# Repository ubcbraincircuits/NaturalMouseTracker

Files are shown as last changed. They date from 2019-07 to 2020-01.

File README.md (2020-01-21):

# MouseTrackingSystem
A system for using RFID tags and computer vision to track multiple mouse movement within a small environment.
For more detailed information, please check the [wiki!](https://github.com/ubcbraincircuits/NaturalMouseTracker/wiki)
For a brief overview, read on!

## RFID System
Uses 4 ID-20LA RFID tag readers, which then interface with the Raspberry Pi with serial communication.
The tag readers are set up in the four corners of the cage, to minimize electromagnetic interference. This system is constantly running in parallel with the Overhead Camera, recording each tag read with respect to frames of the video.

## Overhead Camera
Records videoa at 15.0 fps, converts to grayscale, and saves for use in the object detection system.

## YOLO
An object detection system trained in-house using https://pjreddie.com/darknet/yolo/. Stands for "You Only Look Once" - this system is very fast and accurate, and only fails when mice climb completely atop one another, or are obscured from the camera's vision. The information from the object detection system feeds into the Mouse Trackers.

## Mouse Trackers
When the detection system sees as many objects as there are mice, then the system simply tracks based on Euclidean distance, choosing the closest pairs of detections until all mice and detections are covered. Since the framerate is faster than the mouse movement, this is a reliable method for tracking all mice. When mice are lost, a mouse is removed from the main list and a "dummy mouse" is added in place - so, if two mice are lost, then they are replaced with dummy mice henceforth. Once the mice return, the RFID system is checked continuously. Once we have found a frame in which a mouse has been read by the RFID sensors, the dummy mice are classified and the system is retroactively corrected. In this way, even though we may not be certain of which mouse is which on every frame moving forwards in time, once the system has finished running, all mice movement will have been completely tracked.

### RFID Validation
RFID validation is used to correct and update the current state of the system. If an identity swap occurs that is not handled by the preventative destruction method, then there must be countermeasures. Thus, if a mouse identified by the system as tracked walks over an RFID sensor and is shown to be a different tag, then its data must be removed up to the last validation point, i.e. the last point it was confirmed by an RFID sensor. 

By combining these methods, we can confirm no identity swaps and an 80%+ coverage rating for this system.

### Sources
- https://github.com/Ebonclaw/Mouse-Wearable-Tech---RFID-and-Localization-Grid-Computer-Vision-Enhancement - original inspiration
- https://github.com/AlexeyAB/darknet - object detection 
- https://github.com/jamieboyd/RFIDTagReader - tag reader

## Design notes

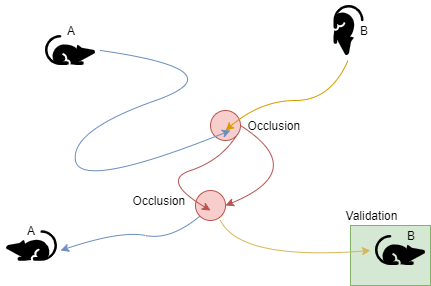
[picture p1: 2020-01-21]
SwapHandling-Page-2.png

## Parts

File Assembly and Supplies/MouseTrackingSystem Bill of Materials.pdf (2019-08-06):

Item | Quantity | Supplier | Individual Cost | Total Cost Part Number
N10 Mouse Cage | 3 Ancare | N/A | N/A | N/A
ID-20LA | 12 SparkFun | $ | 34.95 $ | 419.40 | 11828
RFID USB Reader | 12 SparkFun | $ | 25.18 $ | 302.16 | 9963
Zinc-Plated Alloy Steel
Socket Head Screw,
1/4"-20 x 1" | 3 McMaster-Carr $ | 6.37 $ | 6.37 90128A247
M3 (16mm) 18-
8 Stainless Steel Socket
Head Screw | 100 (pack) McMaster-Carr N/A | $ | 5.87 91292A115
M3 Medium-Strength Steel
Hex Nuts—Class 8 | 100 (pack) McMaster-Carr N/A | $ | 0.88 90592A085
Steel Pan Head Phillips
Screw, M2.5 x
0.45 mm Thread, 12
mm Long | 100 (pack) McMaster-Carr N/A | $ | 4.66 92005A075
M3 (12mm) 18-
8 Stainless Steel Socket
Head Screw | 100 (pack) McMaster-Carr N/A | $ | 4.97 91292A115
M2 (12mm) 18-
8 Stainless Steel Socket
Head Screw | 100 (pack) McMaster-Carr N/A | $ | 4.02 91292A834
M2 Medium-Strength Steel
Hex Nuts—Class 8 | 100 (pack) McMaster-Carr N/A | $ | 1.47 90592A075
M2 Medium-Strength Steel
Hex Nuts—Class 8 | 100 (pack) McMaster-Carr N/A | $ | 1.94 90592A080
RPi Camera (H), Fisheye
Lens, Supports Night
Vision | 3 Waveshare | $ | 31.59 $ | 94.77 | 10703
Raspberry Pi 4/3 B+ | 3 CanaKit | $ | 46.95 $ | 140.85 N/A
| | TOTAL | $ | 987.36
| | Av. Cost | $ | 329.12

Link
http://www.ancare.com/products/cages-and-caging-equipment/rodent-cage/mouse-cagehttps://www.sparkfun.com/products/11828
https://www.sparkfun.com/products/9963

https://www.mcmaster.com/90128A247

https://www.mcmaster.com/91292a115

https://www.mcmaster.com/90592A085

https://www.mcmaster.com/92005A075

https://www.mcmaster.com/91292a115

https://www.mcmaster.com/91292a834

https://www.mcmaster.com/90592A075

https://www.mcmaster.com/90592A080

https://www.waveshare.com/product/mini-pc/raspberry-pi/cameras/rpi-camera-h.htmhttps://www.canakit.com/raspberry-pi-4.html

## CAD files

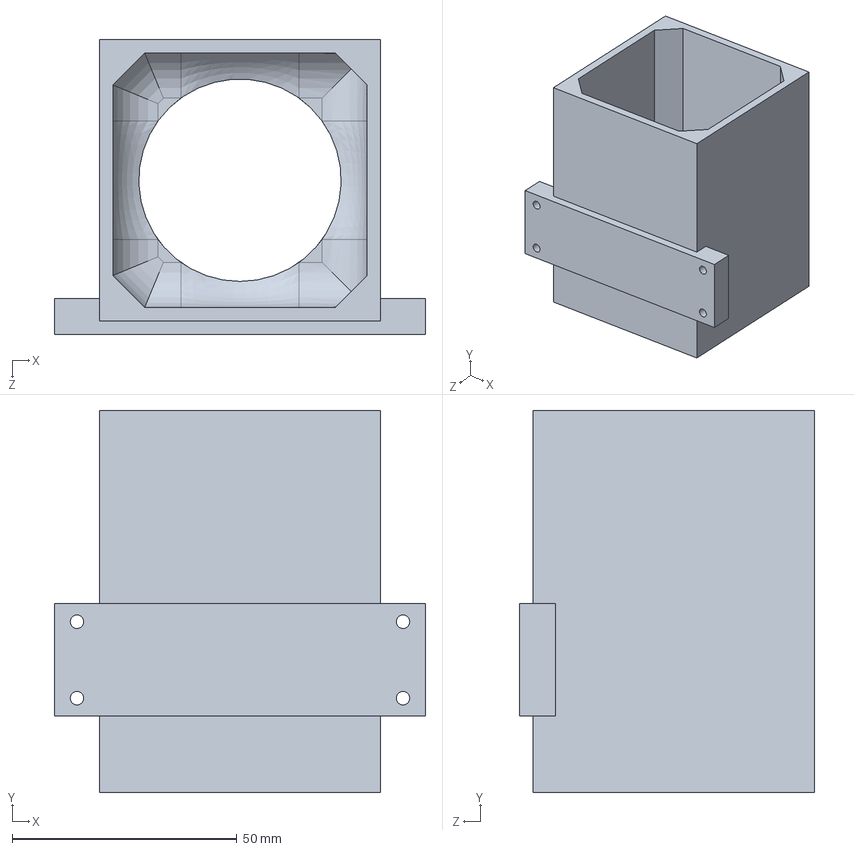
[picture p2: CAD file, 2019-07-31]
CAD Files/WaterBottleHolster.SLDPRT
82.5 x 85.0 x 65.5 mm

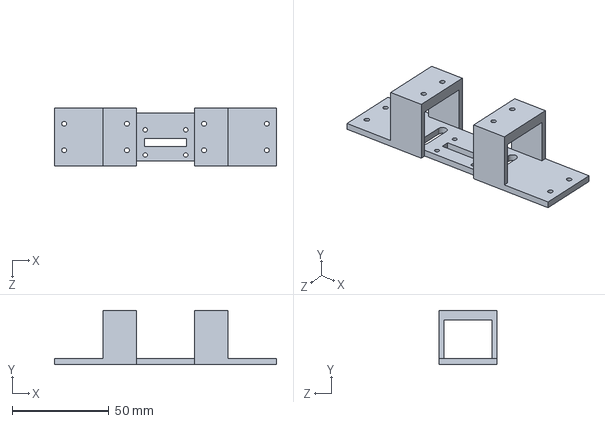
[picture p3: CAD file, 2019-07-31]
CAD Files/Camera LED Mount.SLDPRT
115.0 x 28.0 x 30.0 mm

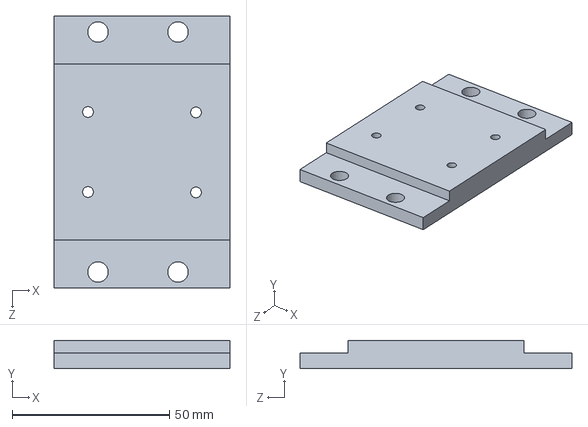
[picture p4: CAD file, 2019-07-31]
CAD Files/Reader Base.SLDPRT
55.9 x 9.00 x 86.4 mm

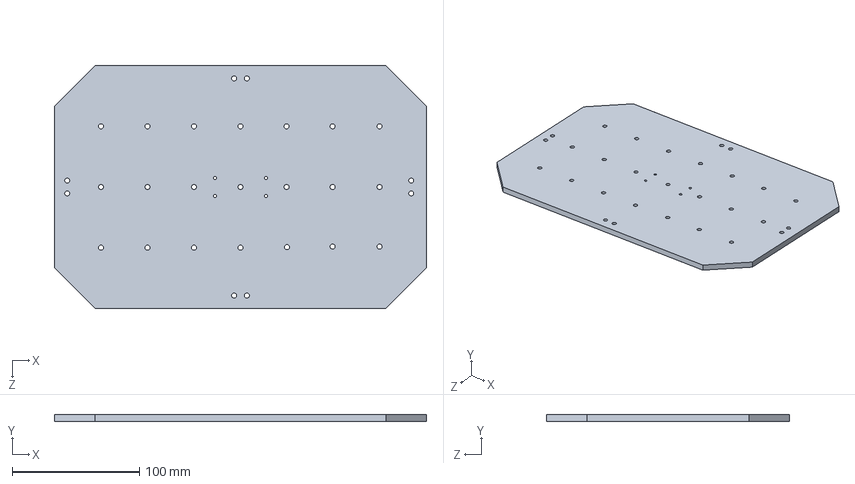
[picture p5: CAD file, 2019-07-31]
CAD Files/Lid.SLDPRT
292.1 x 5.30 x 190.5 mm

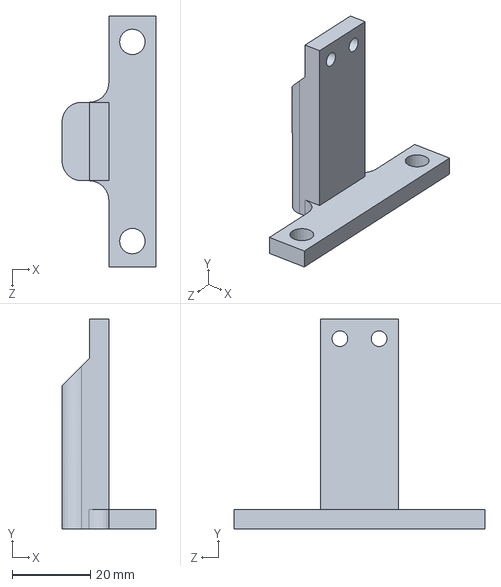
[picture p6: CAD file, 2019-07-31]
CAD Files/Base Attachment.SLDPRT
23.9 x 53.5 x 64.0 mm

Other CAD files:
CAD Files/Base Attachment.STL
CAD Files/Camera LED Mount.STL
CAD Files/Lid.DXF
CAD Files/Reader Base.STL
CAD Files/WaterBottleHolster.STL

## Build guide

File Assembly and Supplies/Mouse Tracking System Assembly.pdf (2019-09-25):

# Mouse Tracking System: Assembly Instructions

## You Will Need:

- A computer with (at minimum) a GPU with 4GB of GPU-RAM
- Access to a 3D printer and a supply of PLA
- Laboratory mice with implanted RFID tags
- Access to a laser/waterjet cutter and ¼” acrylic
- 1 ThorLabs metal platform (fits 3 cages)
- Everything listed in the Bill of Materials

### Step 0: Preparation

a) I recommend cutting the lid piece ahead of time. Make an order with your machine shop (or cut your own, if you can). The air holes do not have to be exact – the screw holes should be relatively precise, which is why I do not recommend doing this by hand. If doing this by hand, measure very carefully and use a drill press to form the holes.
b) Print the 3D-printed pieces: This will take a while, likely overnight, and may take a few passes to fit all the pieces. Ensure you print the water bottle holster in white if you can.
c) Drill 2 3mm holes on each short side of the cage, 25 mm above the floor. Use the base attachment piece as a reference.
d) Drill 4 2.5mm holes on one side of the cage, to match the water bottle holster.

### Step 1: Mechanical Assembly

a) Start with the reader bases. Place the 12mm length M3 bolts through the holes in each breakout board, and screw 4 nuts on the backside to act as spacers. Mount each board on its respective reader, and screw another 4 nuts to fasten them firmly. Repeat for each breakout board.
b) Place the two base attachment pieces with 10 holes (exclusive) between them, flat sides facing inward. Screw them into the platform with the ¼”-20 bolts. The cage should fit nicely between them – if not, count again.
c) Place each reader base with the outward hole side in line with the base attachment piece holes: there should be a line of 6 holes, with the base attachment piece in the middle. These pieces will form the four corners of the cage. Carefully, taking care that the bases stay flush with the platform, screw them in with more ¼”-20 bolts. Alternating the bolt you are screwing in will make this an easier process.
d) Place each RFID reader on its respective breakout board.
e) Either paint the exterior of the cage with nonhazardous white paint, or tape printer paper over the sides, much in the same way as wrapping a package. This ensures a better background for the mice to be seen on. Place the cage on the readers and line up the holes with the base attachment – screw in the 16mm M3 bolts and thread the nuts on the exterior of the cage. The readers should be gently pressing against the floor of the cage.
f) Screw in the camera and LEDs to the mount with the M2/M2.5 bolts, then screw the mount to the lid in the center of the cage.

### Step 2: Software Setup

a) Clone https://github.com/Judge24601/MouseTrackingSystem.git to both your Raspberry Pi and the computer you plan to use for processing the videos. (git clone …)
b) Follow the instructions in https://github.com/AlexeyAB/darknet ‘s README for installing darknet. If using CUDA 10.1, edit the .vcxproj files in build/darknet with a text editor to replace 10.0 with 10.1 – this is necessary or the system will not compile.
c) Unzip darknet.zip in the MouseTrackingSystem folder on your computer. Move the files
darknet_video.py, MouseTracker.py, visualize.py into the darknet folder.
d) If using black mice, you can use the pretrained weights in the repository. Move yolo-obj_best.weights into the folder as well. Otherwise, you will need to train your own network. Follow the instructions in https://github.com/AlexeyAB/darknet to do so. Ensure you prepare 2000+ good quality images – I recommend including non-mouse objects of a similar size and shape to your mice in the dataset. Otherwise, the network can rely too heavily on contrast.

### Step 3: Running the System

a) Before plugging in all your USB cables, ensure that you have set up SSH on your Pi – running the system headless will achieve a better framerate.
b) Plug in your external hard drive, and run the following commands:
a. sudo apt-get update
b. sudo lsblk -o UUID,NAME,FSTYPE,SIZE,MOUNTPOINT,LABEL,MODEL
(note the location, UUID, and FSTYPE of your HDD)
c. (if FSTYPE is EXFAT) sudo apt-get install exfat-fuse
d. (if FSTYPE is NTFS) sudo apt-get install ntfs-3g
e. sudo mkdir /mnt/frameData
f. sudo nano /etc/fstab
g. Add the following line: UUID=<UUID> /mnt/frameData <FSTYPE> defaults,auto,umask=000,users,rw,nofail 0 0
h. Exit nano and sudo reboot
i. This will mount your external hard drive on the Pi automatically upon connection.
j. For any problems, check https://www.raspberrypi.org/documentation/configuration/external-storage.md.
c) Do a test run of the program with a sample RFID tag. Hover the tag over the 4 readers in sequence, and note this sequence. Open the results file, and adjust the readerMap in RFIDReader.py so that it matches the actual sequence. This must be done each time the USBs are unplugged, but not as long as they remain plugged in.
d) Put the mice in the cage, along with food and water. Place the lid with the camera mount on top.
e) To preview the video and check lighting, run preview.sh through ssh. This will open up a stream that you can view on any computer with VLC Media Player (Media -> Open Network
Stream -> rtsp://:8554 )
f) Through ssh, run python RFIDReader.py – let the system run for as long as you want to collect data for. When done, use Ctrl-C to stop the program.

g) Save the photos onto a hard disk drive, and transfer them to your computer. Copy the files you wish to use into “MouseTrackingSystem/darknet/frameData” and copy the RTS_test.txt file into “MouseTrackingSystem/darknet”.
h) Run python darknet_video.py, and enter the tags for your mice.
i) Return later to find a JSON file with all the processed data!

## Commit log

2019-05-16 Arduino complete and 2.25x faster Python
2019-07-05 More framerate improvments
2019-07-09 Removed freezing and duplicate frames
2019-07-30 CAD Files
    [Base Attachment.SLDPRT, Base Attachment.STL, Camera LED Mount.SLDPRT, Camera LED Mount.STL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]
2019-08-06 Lid update
    [Lid.DXF]
2019-08-06 BOM and Assembly Instructions
2019-08-08 updated assembly instructions
2019-09-13 Modification of darknet to be current
2019-09-25 Assembly additions
2019-09-25 Assembly notes
2019-10-18 Kalman filter work + integration
2019-11-29 tracking at max capacity thus far
